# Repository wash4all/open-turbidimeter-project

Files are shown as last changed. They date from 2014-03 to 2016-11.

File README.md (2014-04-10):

# The Open Turbidimeter Project

## Contents
- [Background](#background)
- [What is "Turbidity"?](#what-is-turbidity)
- [Measuring Turbidity](#measuring-turbidity)
- [Goals for the Turbidimeter](#goals-for-the-turbidimeter)
- [Connectivity](#connectivity)
- [Development and Dependencies](#development-and-dependencies)
- [Licensing](#licensing)
- [Funding Sources](#funding-sources)
- [Contact](#contact)

## Background

The high cost of equipment to monitor water quality often puts valuable health tools out of reach for many communities in developing countries. Consequently, millions of people are exposed to health risks that could me mitigated if solutions were available at a price point they can afford. **The goal of our project is to create a low-cost device to measure the turbidity of a water supply.**

## What Is "Turbidity"?

Turbidity refers to the dirtiness or cloudiness of a water sample, and an internationally recognized criterion for assessing drinking water quality because the colloidal particles in turbid water may harbor pathogens, chemically reduce oxidizing disinfectants, and hinder attempts to disinfect water with ultraviolet radiation. Technicians at water treatment plants regularly measure water turbidity before and after treatment. It’s a legal requirement in many countries, and one indicator of whether treated water is safe for human consumption. The unaided eye can distinguish cloudy water from clear water, but even visibly clear samples of water can be dangerous.

## Measuring Turbidity

The quantification of turbidity is complicated by the fact that the goal is to obtain an aggregate quasi-concentration of *all* the different types of particles present in the water. This is different than, say measuring the concentration of a *specific* chemical by adding known quantities of reagents and measuring the mass of the resulting precipitate.

A turbidimeter is an optical instrument that assesses turbidity by measuring the scattering of light passing through a water sample. The general principle is that the more particles are floating around in the water, the more light will be scattered as it passes from on one side of a sample to the other. In its simplest form, a turbidimeter is just a light source and a photosensor arranged perpendicular to each other around a water sample. More complicated setups using multiple sensors and/or light sources extend the detection limit and accuracy of the device. Some possible layouts are shown below.

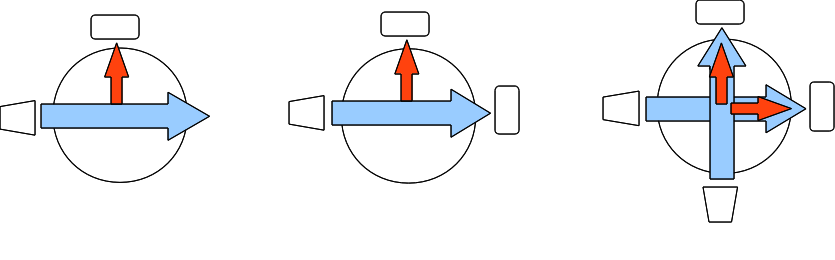
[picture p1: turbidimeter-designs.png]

*Source:* [turbidimeter-designs.png](turbidimeter-designs.png)

Turbidity is most commonly quantified by the Nephelometric Turbidity Unit (NTU)**\***. The NTU scale is defined by reference standards which are created by diluting approved compounds to concentrations designated by the [EPA][EPA Method 180.1] and [ISO][ISO 7027]. The primary standard for this scale is formazin, although other (safer) secondary standards have been approved. Note that these regulations have additional stipulations such as the measurement angle and wavelength of the light source. Looking over the standards themselves is *highly recommended.*

The human eye can detect turbidity levels down to roughly 5 or 10 NTU. Samples of water with turbidity lower than this will appear clear, but may still contain a concentration of colloidal particles sufficient to impair disinfection efforts and may carry a load of contaminants or pathogens sufficient to cause serious human illness. Current EPA regulations stipulate that conventionally treated surface water in the USA must be regularly sampled, that only 5% of samples in a given month may show turbidity greater than 0.3 NTU, and that no sample may show turbidity in excess of 1.0 NTU. Other countries employ different standards, and the World Health Organization (WHO) recommends that turbidity levels be less than 0.1 NTU prior to disinfection.

Handheld units capable of analyzing a single sample vial cost several hundred dollars; automated units capable of intermittently analyzing samples from flowing water can cost several thousand. Partly completed open-source turbidimeter projects can be found online, apparently abandoned.

**\*** Nephelometry is the term given to the side-scatter method of measuring turbidity described above

[EPA Method 180.1]: (http://water.epa.gov/scitech/methods/cwa/bioindicators/upload/2007_07_10_methods_method_180_1.pdf)
[ISO 7027]: http://www.iso.org/iso/catalogue_detail.htm?csnumber=30123

## Goals for the Turbidimeter

1.  Costs less than $100 when economies of scale are applied to production
2.  Reads samples with an accuracy of:
    1.  0.05 NTU from 0-5 NTU
    2.  0.2 NTU from 5-20 NTU
    3.  5% from 20-1000 NTU
3.  Can be operated manually or in automated sampling mode
4.  Has wireless data transmission capability
5.  Uses a replaceable battery pack

An open-source turbidimeter fulfilling the design goals listed above will not quite meet the strict technical requirements of the EPA, but will nonetheless provide a huge improvement over the status-quo of rural and small-scale water treatment monitoring, at a realistic cost.

## Connectivity

The intent is for these devices to be deployed at rivers, wells, and treatment plants in possibly very remote areas that are visited infrequently by engineers and regulators from more urban areas. For this reason, the device will be integrated with a remote data-acquisition system to enable record keeping, troubleshooting, and real-time observation of water quality. We are exploring a few different ways of getting data off the device wirelessly.

**Bluetooth** ```tested``` ```firmware support```
Include a low-power Bluetooth module that sends data to a linked Android cellphone, which uses its data plan and SMS to sync to a remote server. The problem with this is that the cost of a smartphone doubles or triples the cost of the device. The phone itself is also subject to damage or theft, which cripples the data connection. The additional processing power and memory afforded by a smartphone, on the other hand, are attractive features.

**GSM Modem** ```tested``` ```firmware support```
Integrate a GSM modem (the core piece of technology used by mobile phones) into the turbidimeter itself to provide wireless connectivity. This is a less expensive approach, but has issues with reliability and increases power consumption *quite a bit*. We also want to encourage DIYers to build their own units, and prototyping GSM modules like the one sold by Arduino are still not cheap. Therefore we want to make sure that the turbidimeter can still be used without wireless capability if we go with this approach.

**Direct Connection to Mobile Phone** ```not tested``` ```no firmware support```
Connect the turbidimeter to an arbitrary mobile phone using a wired connection. This requires the hardware to support the connection (most likely a USB host adapter), but in theory any GSM-compliant phone would be controllable using it. Here's an example of an [Arduino-controlled Motorola Razr](https://www.circuitsathome.com/mcu/programming/interfacing-arduino-to-a-cellular-phone).

## Development and Dependencies

In the prototyping stage, most of the development is done using rapid prototyping tools like Arduino and 3D printed parts. We expect to transition off these tools soon as we finish designing custom components, although it will always be possible to build your own turbimeter by printing the parts and assembling the necessary circuitry.

A list of software and hardware dependencies is maintained in the file [Dependencies.md](Dependencies.md). We try to use all open-source design tools, although we are stuck with a few non-free packages at the moment. For these cases, we export to open formats (such as STL, STEP, and BRD).

Issue tracking, package releases, and the like are managed through GitHub, which is most likely where you are reading this anyways. To download the revision-controlled repository with all the latest code, use ```git clone https://github.com/wash4all/open-turbidimeter-project.git```. Alternately you can browse the [releases][] for a stable set of files that are known to work.

[releases]: https://github.com/wash4all/open-turbidimeter-project/releases

## Licensing

The software and documentation for the project are covered by the [GNU General Public License][gpl] and [Creative Commons ShareAlike-Attribution][cc] licenses, respectively.

[gpl]: https://www.gnu.org/copyleft/gpl.html
[cc]: https://creativecommons.org/licenses/by-sa/4.0/

## Funding Sources

The Open Turbidimeter Project has been funded in part by EPA Grant Number [SU835517][grant]: "Smart" Turbidimeters for Remote Monitoring of Water Quality.

[grant]: http://cfpub.epa.gov/ncer_abstracts/index.cfm/fuseaction/display.abstractDetail/abstract/10094/report/0

## Contact

Development of the Open Turbidimeter Project is facilitated by [WASH for All][], an organization working for universal access to clean drinking water and sanitation by developing innovative and cost-effective tools.

Contact [Chris][] or [Alex][] if you'd like to get involved with WASH for All or if you have questions about the project or the organization.

[WASH for All]: http://wash4all.org
[Chris]: mailto:iamchriskelley@gmail.com
[Alex]: mailto:amk283@cornell.edu

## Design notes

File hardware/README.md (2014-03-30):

# Construction and Usage of the Turbidimeter

## Introduction

The sections below detail the necessary parts and tools, wiring, assembly, and microcontroller programming to get up and running with the Open Turbidimeter Project. You are encouraged to contact the team members with any questions about the construction, operation, or expansion of this device.

## Components List

All components of the open-source turbidimeter are indicated in the [Parts List](Parts List.tsv), along with potential
distributors. Indicated costs are for individual pieces and do not include shipping and handling or taxes.

## Structural Components

The open-source turbidimeter case consists of four different parts: (1) bottom, which includes ports for button and on/off switch; (2) cuvette holder, which houses the sensor and light source and holds the glass cuvette during device operation; (3) top, which has openings for the seven-segment LED display and the top of the cuvette holder; and (4) battery lid, which slides out from the case assembled case top and bottom to expose the battery holder. Electronic files of these objects (in STL format) are available in the [3D Design Files](3D Design Files/) folder. Note that any container that provides good shielding from incidental light may suffice for the larger portion of the case (e.g. a nested pair of cardboard boxes).

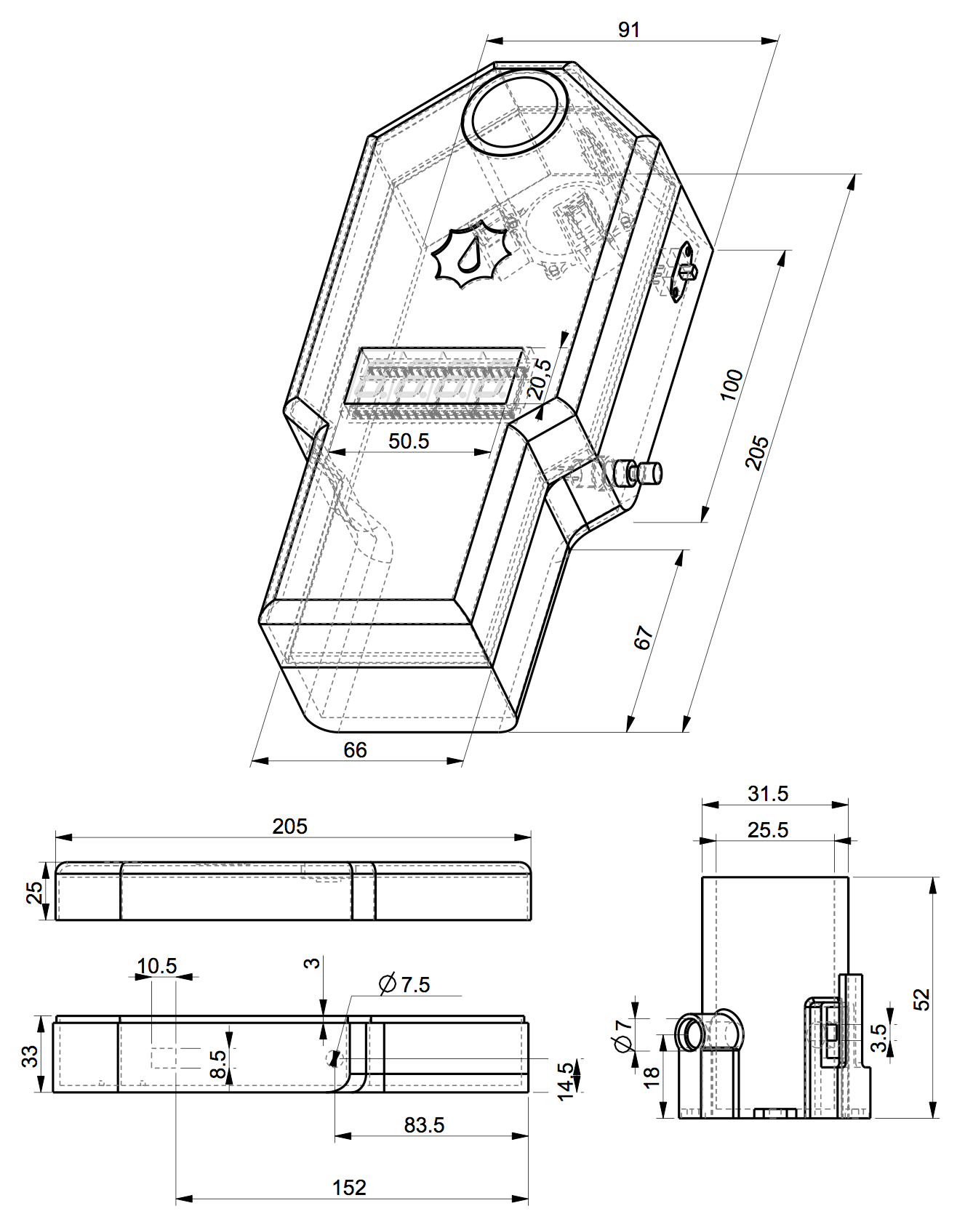
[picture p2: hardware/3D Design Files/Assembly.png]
Assembly

Link: [Assembly.png](3D Design Files/Assembly.png)

_**Fig 1** Image of the open-source turbidimeter with major dimensions given. The four smaller images (left to right) are the case lid (top left), the case base (bottom left), the battery lid (top right), and the cuvette holder (bottom right). All dimensions are in millimeters._

## Tools

A utility knife, soldering iron, and solder are required for assembly of the open-source turbidimeter, and safety goggles are recommended. To replicate the printed four-part case, one must have access to a 3D-printer with black ABS filament. The microprocessor can be programmed via a USB-to-Serial adapter (Mouser carries one [#A000059] for $14.95) or with an Arduino (as described in this [tutorial](http://arduino.cc/en/Tutorial/ArduinoToBreadboard). Electrical tape is very helpful (for grouping wires
together), as are a pair of wire strippers.

## Turbidimeter Breadboard and Schematic

The microprocessor and connected components of the open-source turbidimeter are depicted below in Fritzing (Figure S2) and EAGLE formats (Figure S3). Figure S2 depicts what the device looks like internally, while Figure S3 is a more formal schematic.

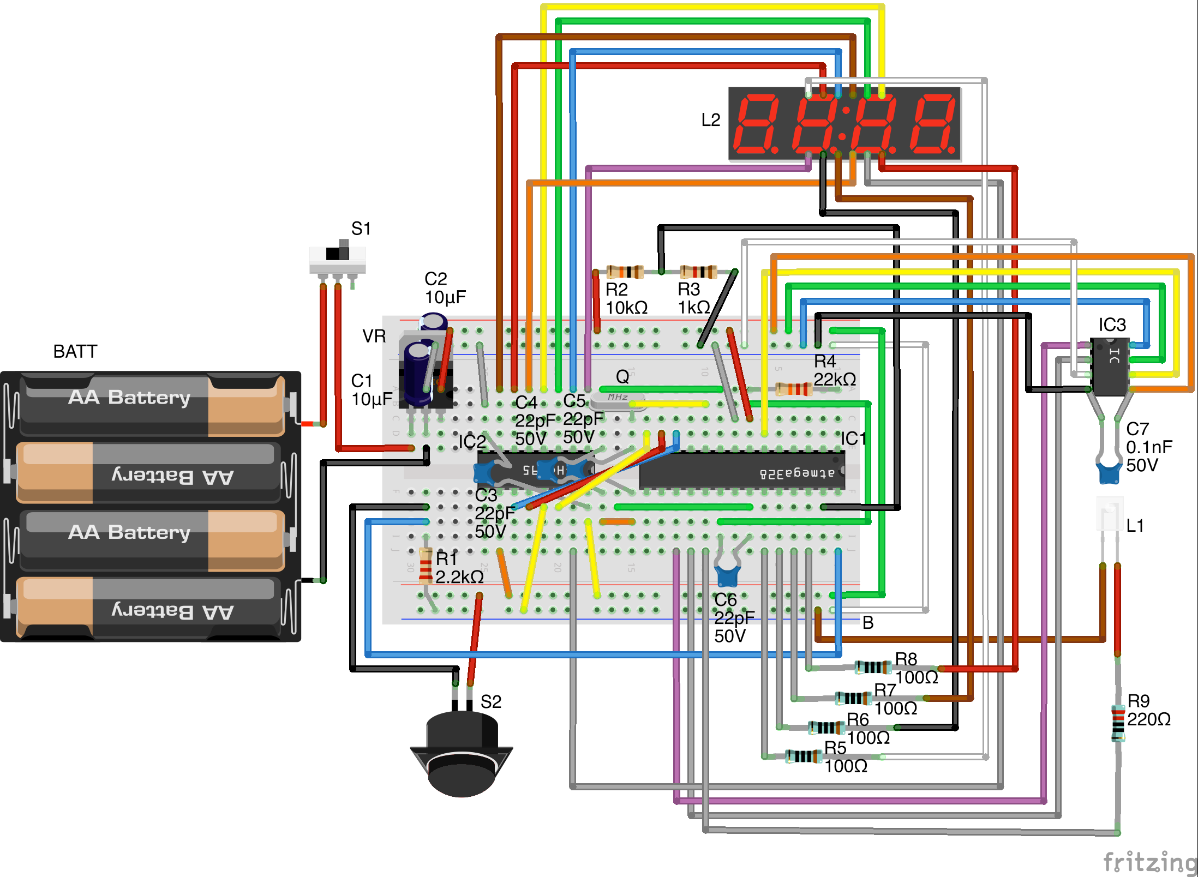
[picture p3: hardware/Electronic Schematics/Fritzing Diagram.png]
Fritzing Diagram

Link: [Fritzing Diagram](Electronic Schematics/Fritzing Diagram.png)
	
_**Fig 2** Depiction of the internal components of the open-source turbidimeter (components labels cross-referenced in the parts list and Figure S3)_

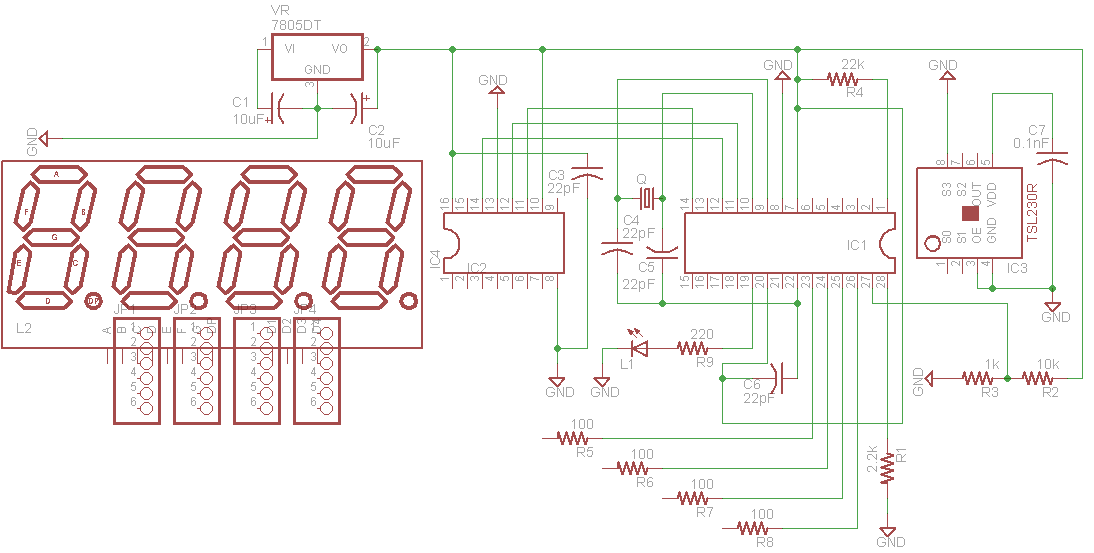
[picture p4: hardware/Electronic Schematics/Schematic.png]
Circuit Schematic

Link: [Circuit Schematic](Electronic Schematics/Schematic.png)

_**Fig 3** Schematic of the circuit board for the open-source turbidimeter (components labels cross-referenced in Table S1 and Figure S2)._

## Basic Assembly Instructions

1.  Gather the components listed in Section 1, and the tools listed in Section 3.
2.  Print the parts described in Section 2 (or devise your own light-shielding case).
3.  Wire together the internal components of the open-source turbidimeter according to Figures 2 and 3. Here are some key points:
    1.  It's hard to see some connections of the circuit, such as the wiring of the voltage regulator (VR1), on Figure 2. The Arduino website has a well-illustrated tutorial on wiring the ATMega328P microprocessor (http://arduino.cc/en/Main/Standalone) that the reader may find useful.
    2.  The semi-circles on the microprocessor (IC1) and shift register (IC2) indicate orientation of these components. It is vital that chips are aligned properly using these guides. Wiring them in the opposite orientation will destroy the chips once voltage is applied! Please note that the semi-circle on the TSL230R sensor in Figure 2 is merely a visual aid, and is not present on the actual chip.
    3.  The pins of the seven-segment display are diagrammed by the distributor Electrodragon (http://www.electrodragon.com/w/index.php?title=7-Segment_Display). The linked document maps pin placement to function and representation in Figure 3 (e.g., the bottom left pin on the seven-segment display is pin 12, which maps to segment E of the display, which connects to port QE on the shift register).
    4.  Resistors R2 and R3 combine to form a voltage divider, which is used to measure the voltage provided by the batteries. To achieve useful results, use resistors with tolerance of 1% or less. Tolerance levels of 5% are suitable for the other resistors in the device.
    5.  The internal components list generally should be followed closely, however the power switch (S1) and button (S2) can easily be changed to suit the builder's aesthetic.
    6.  As always, exercise caution. Do not attempt construction of any electrical device without knowledge of proper technique and safety.

## Programming

The files included in the ```software``` folder of the project need to be compiled and uploaded to the microcontroller to get the device working. Connect the device to a computer using a properly wired [USB-to-Serial adapter](http://arduino.cc/en/Main/USBSerial) (this requires the use of an additional 100nf capacitor) or an [Arduino board](http://arduino.cc/en/Tutorial/ArduinoToBreadboard). Then install the [Arduino programming environment](http://arduino.cc/en/main/software). After followng the instructions in the sofware readme to install the necessary libraries, open the ```turbidimeter.ino``` program in the Arduino software and upload it to the microcontroller.

You're ready to go!

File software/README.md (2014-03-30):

# Software

This directory contains the _firmware_ for the turbidimeter. These are the files that are compiled and uploaded to the microcontroller and provide the user interface, measurement, and calibration functions.

Contents:

The folder called ```turbidimeter``` is the [Arduino](http://arduino.cc/en/main/software) project folder for the turbidimeter firmware. This can go anywhere and you can rename it, but the ```.ino``` file must have the save name as the parent folder when working in the Arduino IDE. This is the file that you most likely be working with if you want to change how the turbidimeter operates.

The ```libraries``` folder contains the extra libraries needed to compile the Arduino sketches, providing the ability to send/receive text messages, store calibration data, etc. These need to be made available to the Arduino compiler by putting them in a place it knows about. One sure way to do this is to import them using the "Sketch>Import Library" utility in the Arduino IDE. Depending on how you have installed Arduino, this should have the effect of copying the files into the ```C:/Users/You/Documents/Arduino/libraries``` folder (Windows) or ```~/sketchbook/libraries``` folder (Mac/Linux). Note that some of the libraries have the same name as those prepackaged with the Arduino software. They are different (usually slightly modified for interoperability reasons); if you run into errors, make sure you are using the right ones.

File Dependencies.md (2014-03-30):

# Guide to File Extensions

A list of the file types you may encounter in this project. We have attempted to restrict the software dependencies to free programs as much as possible, with a few exceptions (and we are working on those).

-  ```.sch``` [Eagle](http://www.cadsoftusa.com/eagle-pcb-design-software/?language=en) circuit schematic
-  ```.brd``` [Eagle](http://www.cadsoftusa.com/eagle-pcb-design-software/?language=en) printed circuit board file
-  ```.ods``` Open Document Spreadsheet file (supported by Excel, LibreOffice, etc.)
-  ```.stl``` 3D part file that can be used to send parts to a 3D printer or production service
-  ```.scad/escad``` [OpenSCAD](http://www.openscad.org)/[extended OpenSCAD](http://www.implicitcad.org) code used to generate 3D part files
-  ```.part``` Proprietary [PTC Creo](http://www.ptc.com/product/creo/) CAD file. We try to provide open source equivalents to these files as much as possible, because CAD software can be very expensive.
-  ```.md ``` [Markdown](https://help.github.com/articles/markdown-basics) file. Just a text file with standardized syntax for headings and things. 
-  ```.ino``` [Arduino](http://www.arduino.cc) program
-  ```.c/.h/.pde``` C source files for Arduino libraries

**See also:** [Parts List](hardware/Parts List.tsv)

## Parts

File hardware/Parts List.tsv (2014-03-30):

Qty | Name | Description | Vendor | Part # | Unit Price | Price
1 | IC1 | 8-bit Microcontroller | Mouser Electronics | ATMEGA328P-PU | 2.24 | 2.24
1 | Q1 | 16MHz 18pF HC49S Crystals | Mouser Electronics | HC49US-16.000MABJ-UB | 0.58 | 0.58
1 | VR1 | 5V Voltage Regulator | Mouser Electronics | LM7805CT | 0.69 | 0.69
1 | IC2 | 595 Shift Register | Mouser Electronics | SN74HC595N | 0.63 | 0.63
2 | C1,2 | 10uF Capacitor | Mouser Electronics | UKL1C100MDD1TA | 0.15 | 0.3
4 | C3-6 | 22pF Capacitor | Mouser Electronics | 1C10C0G220J050B | 0.015 | 0.06
1 | C7 | 0.1nF Capacitor | Mouser Electronics | 140-50S5-101J-RC | 0.06 | 0.06
1 | R1 | 1/4 Watt 2.2 kOhm Resistor | Mouser Electronics | MF1/4DCT52R2201F | 0.06 | 0.06
1 | R2 | 1/4 Watt 10 kOhm Resistor | Mouser Electronics | MF1/4DCT52A1002F | 0.06 | 0.06
1 | R3 | 1/4 Watt 1 kOhm Resistor | Mouser Electronics | MFS1/4DCT52R1001F | 0.13 | 0.13
1 | R4 | 1/4 Watt 22K Ohm Resistor | Mouser Electronics | MF1/4LCT52R223J | 0.07 | 0.07
4 | R5-8 | 1/4 Watt 100 Ohm Resistor | Mouser Electronics | MF1/4DC1000F | 0.06 | 0.24
1 | R9 | 1/4 Watt 220 Ohm Resistor | Mouser Electronics | MF1/4CCT52R2000F | 0.14 | 0.14
1 | B1 | Breadboard* | Electrodragon | 5205940 | 0.23 | 0.23
1 | - | M/F Jumper Wires (22 count) | Electrodragon | 5101606 | 1.2 | 1.2
1 | S2 | Black Button | Mouser Electronics | 104-0013-EVX | 0.91 | 0.91
1 | L1 | 860nm Infrared LED | Mouser Electronics | W53SF6C | 1.12 | 1.12
1 | L2 | 7-Segment Display | Electrodragon | 4103417 | 0.35 | 0.35
1 | IC3 | TSL230R Sensor | A-Wit | CS454000 | 5.94 | 5.94
1 | BATT | 4xAA Battery Holder | Mouser Electronics | 12BH348-GR | 1.15 | 1.15
1 | - | Printed Cuvette Holder** | -- | -- | 1.42 | 1.42
1 | - | Printed Turbidimeter Encasing** | -- | -- | 7.55 | 7.55
2 |  | Glass Cuvette – 27mm diameter | (Various) | -- | 0.5
1 |  | GSM Modem | Mouser Electronics | A000043 | 88.95

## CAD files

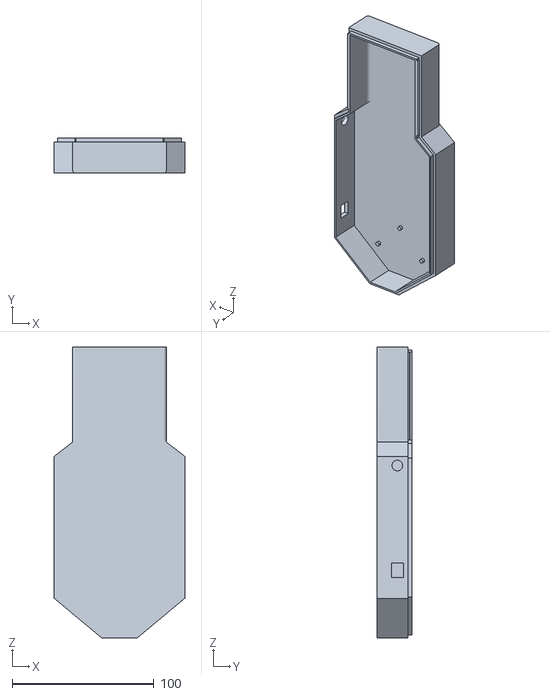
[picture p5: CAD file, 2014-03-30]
hardware/3D Design Files/case_bottom.stl
92.0 x 25.0 x 205.0

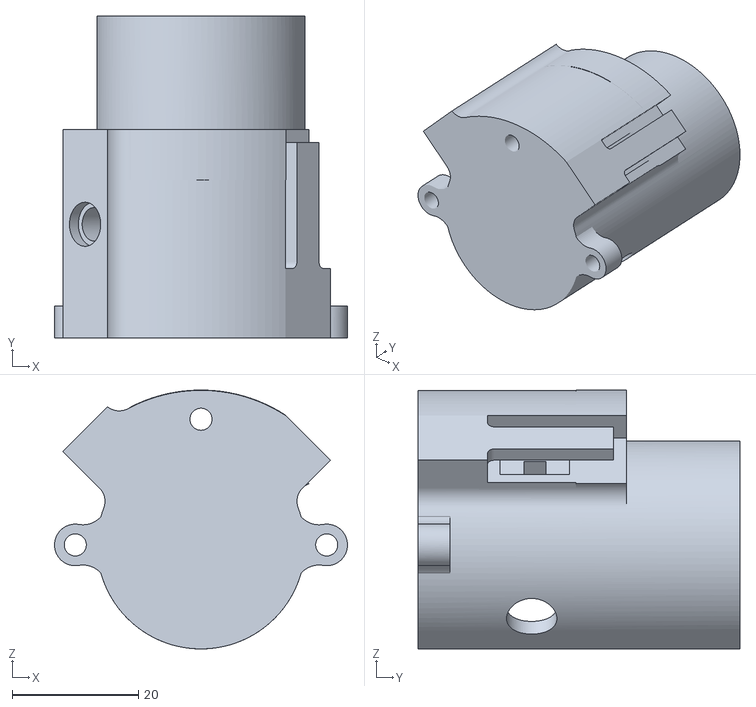
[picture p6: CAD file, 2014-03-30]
hardware/3D Design Files/sample_chamber.stl
46.5 x 51.0 x 41.1

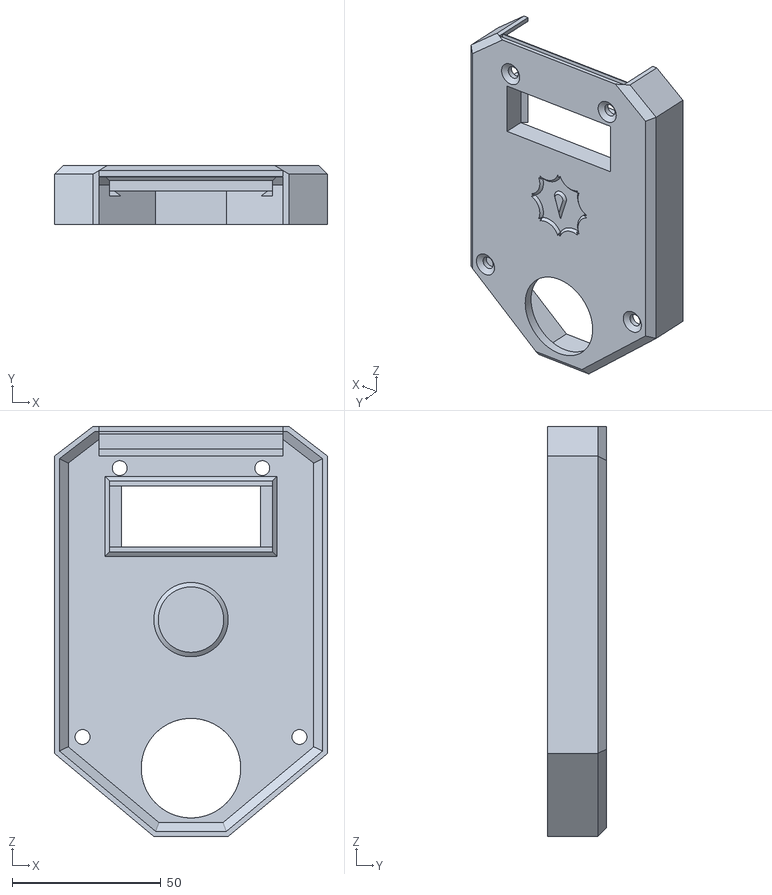
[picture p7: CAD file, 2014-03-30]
hardware/3D Design Files/case_top.stl
92.0 x 20.0 x 138.0

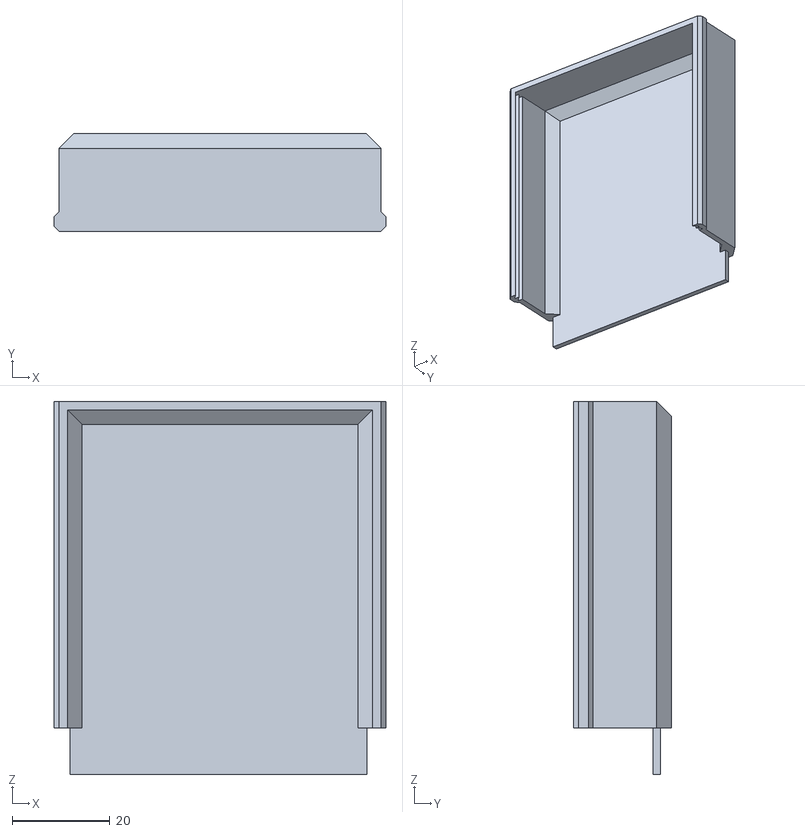
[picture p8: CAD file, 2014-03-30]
hardware/3D Design Files/battery_cover.stl
68.0 x 20.0 x 76.5

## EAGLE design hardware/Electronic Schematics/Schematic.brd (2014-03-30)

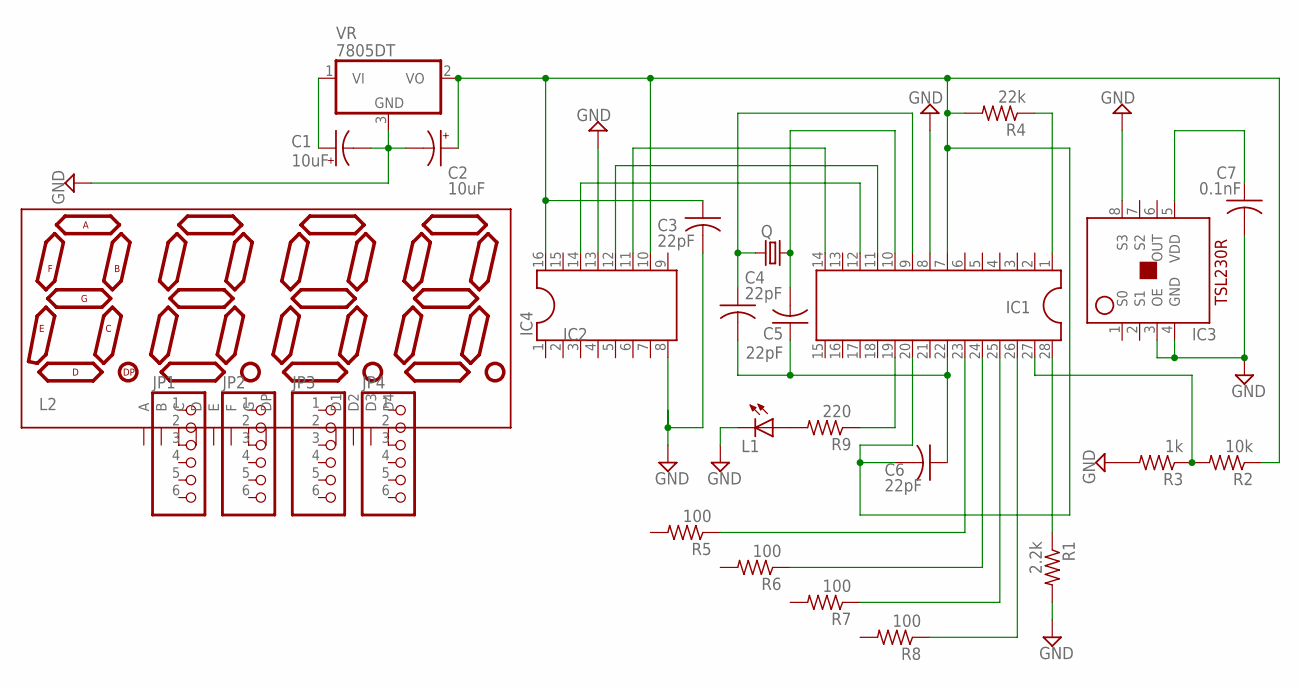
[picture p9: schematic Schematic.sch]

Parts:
C1, C2: 10uF; 140CLH-1010
C3, C4, C5, C6: 22pF; C025-024X044
C7: 0.1nF; C025-024X044
IC1: DIL28; DIL28-6
IC3: LIGHT_TO_FREQ_CONVERTER
IC4: DIL16
JP1, JP2, JP3, JP4: PINHD-1X6CLEAN; 1X06-CLEAN
L1: LEDIRL80A; IRL80A
Q: CRYSTALHC49S; HC49/S
R1: 2.2k; 0207/12
R2: 10k; 0207/12
R3: 1k; 0207/12
R4: 22k; 0207/12
R5, R6, R7, R8: 100; 0207/12
R9: 220; 0207/12
U$1: 7-SEGMENT-4DIGIT-COUNTERPTH; 7-SEGMENT-4DIGIT-COUNTER
VR: 7805DT; TO252

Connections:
GND: C1.-, C2.-, C3.2, C7.2, IC1.8, IC3.3 (OE), IC3.4 (GND), IC3.8 (S3), IC4.8, IC4.13, L1.K (C), R1.2, R3.2, VR.3 (GND)
unnamed: IC1.24, R6.1
unnamed: IC1.23, R5.1
unnamed: IC1.25, R7.1
unnamed: IC1.26, R8.1
unnamed: IC1.28, R1.1
unnamed: IC1.19, R9.1
unnamed: L1.A, R9.2
unnamed: IC1.11, IC4.12
unnamed: C4.2, C5.1, C6.1, IC1.22
unnamed: C1.+, VR.1 (VI)
unnamed: JP1.3, U$1.4 (C)
unnamed: IC1.12, IC4.14
unnamed: C4.1, IC1.9, Q.2
unnamed: C2.+, C3.1, C6.2, IC1.7, IC1.20, IC4.10, IC4.16, R2.1, R4.2, VR.2 (VO)
unnamed: IC1.1, R4.1
unnamed: IC1.14, IC4.11
unnamed: C7.1, IC3.5 (VDD)
unnamed: JP2.3, U$1.5 (G)
unnamed: JP4.3, U$1.6 (D4)
unnamed: IC1.27, R2.2, R3.1
unnamed: C5.2, IC1.10, Q.1

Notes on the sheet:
IC2
IC3

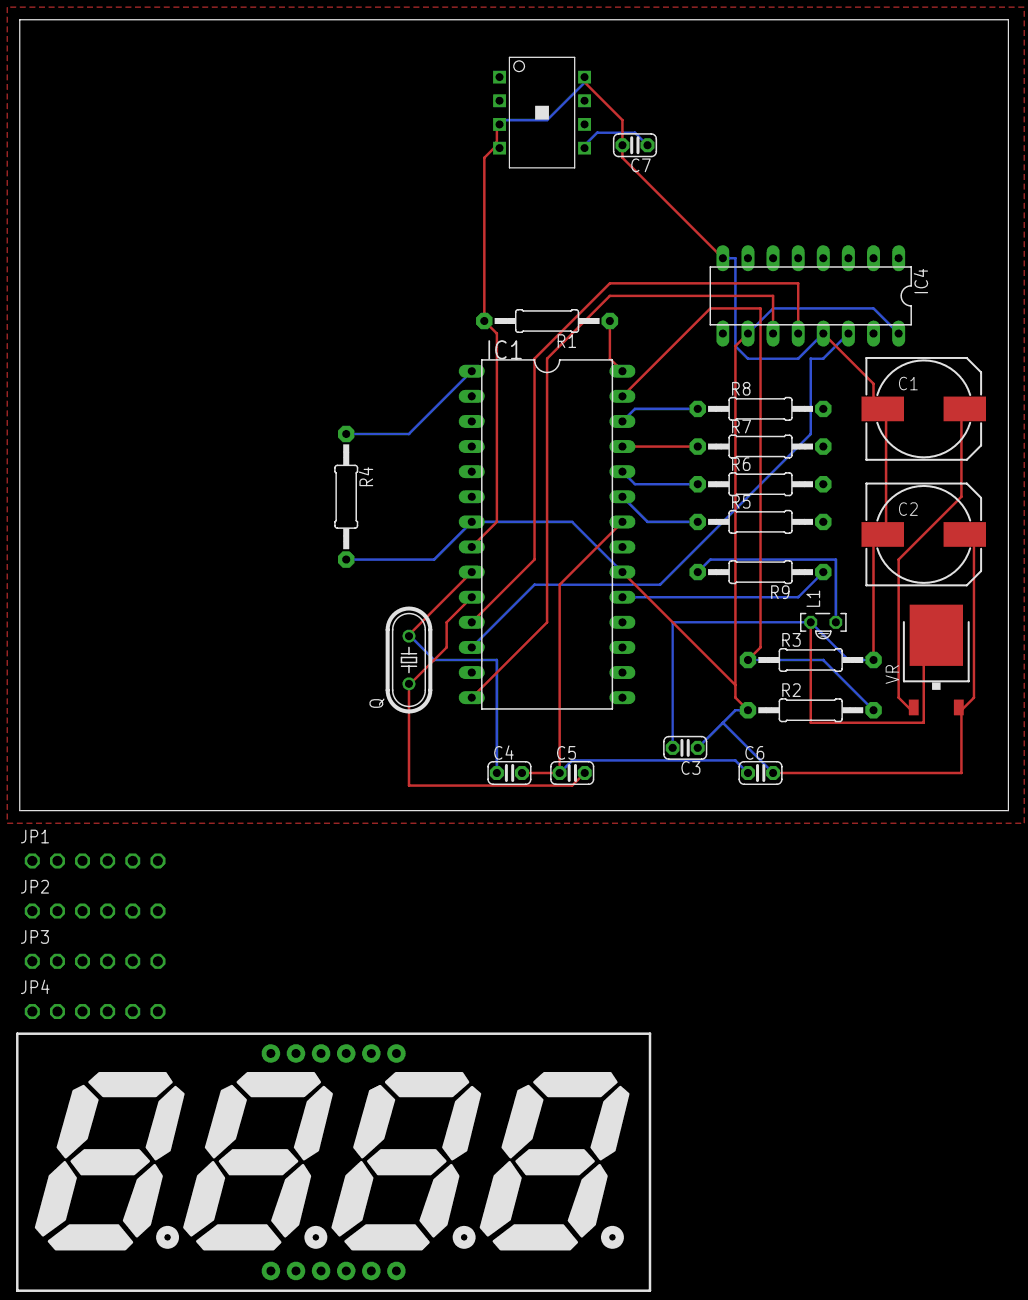
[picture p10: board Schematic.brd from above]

Board: 2 copper layers, 100.0 x 80.0 mm, 27 parts (0 on the bottom side), 22 nets.

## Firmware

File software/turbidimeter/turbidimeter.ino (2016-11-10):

/*--------------------------OPEN TURBIDIMETER PROJECT------------------------*/
/*------------------------------- ARDUINO CODE ------------------------------*/
/*---Developed by WASH4All, 2014. See wash4all.org for further information.--*/

// Flags
const boolean debug=false;  // to reset memory to default config -> true
const boolean using_modem=false; // if not using a GSM modem, change to false
  
// Libraries
// NOTE: Be sure to use the libraries included with this sketch
// (by placing them in your Arduino or Sketchbook folder)
#define NO_PORTD_PINCHANGES
#define NO_PORTC_PINCHANGES
#include <GSM.h>
#include <PinChangeInt.h>
#include <EEPROM.h>
#include <EEPROMAnything.h>
#include <avr/interrupt.h>
#include <avr/power.h>
#include <avr/sleep.h>
#include <avr/io.h>

// Definitions
#define PINNUMBER "1111" // PIN Number for SIM card
#define VERSION_BYLINE "Open Turb Prj\nBIOS v1.11\n2014-04-08\n"
#define IR_LED    4    // light source
#define TSL_S1   12    // S1 and S0 are pins on the TSL230R chip
#define TSL_S0   11
#define TSL_FREQ 13    // frequency signal from the sensor
#define BPIN     A5    // external button
#define BUTTON_EVENT_VALUE 1000

/* 
   Change boolean value, and switch out commented and uncommented the following two 
   pairs of lines below to switch from common cathode to common anode seven-segment display
   NB: For the seven-segment display listed in the Supplementary Materials document, to distinguish
   common cathode and common anode models, look on the side of the display for the numbers '0.56'. 
   If that number is followed by a plus () sign, the display is common cathode.
*/

#define common_cathode_display 1 //if using a common-anode seven segment display, change to false (0)
#if common_cathode_display
#define SEVEN_SEG_NUMBERS {B11000000,  B11111001,  B10100100,  B10110000, B10011001,  B10010010,  B10000010,  B11111000, B10000000,  B10010000,  B01111111,  B10111111, B11111111}
#define SEVEN_SEG_LETTERS {B10101111,  B10000110,  B10100001,  B10010001, B11000111,  B10010010,  B10000111,  B11000000}
#else
#define SEVEN_SEG_NUMBERS {B00111111,  B00000110,  B01011011,  B01001111, B01100110,  B01101101,  B01111101,  B00000111, B01111111,  B01101111,  B10000000,  B01000000, B00000000}
#define SEVEN_SEG_LETTERS {B01010000,  B01111001,  B01011110,  B01101110, B00111000,  B01101101,  B01111000,  B00111111}
#endif

// Gauge voltage by comparison to ATMega328P's internal 1.1v
// R1 and R2 form a voltage divider, with V_out = V_in * R2 / (R1  R2)
#define VPIN     A4    // read voltage from this pin
#define DIV_R1 10000   // resistance for R1
#define DIV_R2  1000   // resistance for R2
#define SAMPLING_WINDOW 1000    // milleseconds between frequency calculations
#define HIGH_SENSITIVITY  100   // sensitivity settings, set via S0 and S1 pins
#define MED_SENSITIVITY   10    // ...
#define LOW_SENSITIVITY   1     // ...
#define READ_REPS 6    // number of readings the turbidimeter will take per 
// button press (average is used for reporting)

// Set up GSM library
GSM gsmAccess;  //US band:"GSM850_EGSM_DCS_PCS_MODE"
GSM_SMS sms;
boolean notConnected = true;

// Global Vars
int  scale_divider = 2, sensitivity = HIGH_SENSITIVITY;     
// scale_divider must match hardwired TSL_S2 and TSL_S3 settings, 
// sensitivity sets TSL_S0 and TSL_S1 settings
// see TSL230R user's guide for more information
int bpress = 1023;   
//variable for digital mapping of analog button press event
float div_fact = 1;  
//division factor, to normalize sensor output by voltage level
long freq_jump_hi = 50000, freq_jump_lo = 4000;            
// (These settings could be used to dynamically set sensor sensitivity,
// e.g. for detecting very bright light levels)
unsigned long timer, frequency;                              
volatile unsigned long pulse_count = 0;  
//interrupt variable; stores count data coming from sensor
boolean bpressed = false, sufficient_battery = true;
const int num_displays = 4;                                  
const int shift_latch = 5;  // RCLK                           
const int shift_clock = 8;  // SRCLCK
const int shift_data = 6;   // SER
// The above three pins connect the 74HC595 shift register
const int dispPorts[num_displays] = {A3,A2,A1,A0};
String language = "espanol"; //"english";
char serialInput;

// Characters: 0-9, '.', '-', blank                   
const byte SevenSegNumbers[13] = SEVEN_SEG_NUMBERS;
  
// Characters: rEdYLStO
const byte SevenSegLetters[8] =  SEVEN_SEG_LETTERS;

// Use this structure for storing data & retrieving data persistently in EEPROM
struct config_t{
  int foo;           //example
  long machine_id;   //example
  unsigned long last_calibration_timestamp; // in seconds since 1/1/1970 12:00a
  // define calibration constants for 5 calibration curves
  // y is the lower bound, m is the slope, b is the the y-intercept (y=mxb)
  float y0, y1, y2, y3, y4,
  m0, m1, m2, m3, m4,
  b0, b1, b2, b3, b4;
  char* remoteNum;
  char* selfNum;
  String userfn; // First name of the person using the device
  String useremail; // Email address of the person using the device
  char* userpn; // Phone number of the person using the device
  String username; // Username for Open Source Water server
  String password; // Password for Open Source Water server
} config;

/*---------------------------------------------------------------------------*/
/*--------------------------------FUNCTIONS----------------------------------*/
/*---------------------------------------------------------------------------*/

void setup() {
  // Set up serial commication
  Serial.begin(9600);
  Serial.println(VERSION_BYLINE);
  Serial.println("Press r to read, c to calibrate.");
  // Pin I/O settings
  pinMode(TSL_FREQ, INPUT); // light sensor
  pinMode(TSL_S0, OUTPUT);  // light sensor
  pinMode(TSL_S1, OUTPUT);  // light sensor
  pinMode(IR_LED, OUTPUT);  // light source
  pinMode(BPIN, INPUT); // button
  pinMode(VPIN, INPUT); // voltage
  pinMode(shift_latch, OUTPUT); // shift register
  pinMode(shift_clock, OUTPUT); // shift register
  pinMode(shift_data,  OUTPUT); // shift register
  for(int i = 0; i < num_displays; i){
    pinMode(dispPorts[i], OUTPUT);
    // set display pins to output
  }

  // Startup procedure
  digitalWrite(IR_LED, LOW);  // light source off
  delay(200);
  turnOffDisplay();
  setSensitivity(sensitivity); // set sensor sensitivity
  timer = millis();
  displayForInterval(-1, "dashes", 1000);

  // Prepare sensors  
  if(divisionFactor_TSL230R() < 0){
    sufficient_battery = false;
    displayForInterval(-1, "error", 2000);
  }
  else{
    displayForInterval(-1, "ready", 2000);
    turnOffDisplay();
  }

  if(debug){
    config.foo = 255;                               
    config.machine_id = 11111111;
    config.last_calibration_timestamp = 1390936721;
    config.y0 = 0;                                  
    config.m0 = 0.02876;                              
    config.b0 = -2.224;                              
    config.y1 = 87.63;
    config.m1 = 0.039;
    config.b1 = -3.124;
    config.y2 = 276.94;
    config.m2 = 0.04688;
    config.b2 = -5.298;
    config.y3 = 2472.3;
    config.m3 = 0.05223;
    config.b3 = -18.525;
    config.y4 = 6049;
    config.m4 = 0.0721;
    config.b4 = -138.9;
    config.remoteNum = "14109278905";
    config.selfNum = "1410*******";
    config.userfn = "****";
    config.useremail = "***@****.org";
    config.userpn = "1410*******";
    config.password = "******";
    config.username = "******";
    
    EEPROM_writeAnything(0, config);
    // Write example calibration settings to EEPROM memory
  }
  else{
    EEPROM_readAnything(0, config);
    // Read calibration data from EEPROM memory
  }
}

void loop() {
  // Given there is enough battery power for the  sensor,
  // - read sensor value for given number of times,
  // - display the resulting value for 4000 milliseconds,
  // - clear out register pins, for a clean display next 
  //   time device is powered off/on.
  // - build a text message and transmit,
  // - check for and parse incoming messages,
  //   if using_modem flag is set to true.  
  // - check for incoming serial commands and process them.
  boolean sufficient_battery = true;
  float reading;
  if(sufficient_battery){
    // SERIAL CONTROL OPTIONS
    serialInput = 'x';
    if (Serial.available() > 0) {
      serialInput = Serial.read(); // get one-byte command option
      Serial.println((char)serialInput); // tell the user what they pressed
    }    
    // check for button press event (0 = pressed)
    bpress = analogRead(BPIN); 
    if (bpress >= BUTTON_EVENT_VALUE || serialInput == 'r'){
      bpressed = true;
      divisionFactor_TSL230R();                
      // read, but discard first reading
      div_fact = divisionFactor_TSL230R();     
      // take another reading of voltage divider
      if(div_fact < 0){
        Serial.println("Battery low...");
        sufficient_battery = false;
      }     
      else{ 
        Serial.println("Taking reading...");        
        reading = takeReadings(READ_REPS);
        Serial.print(reading); 
        Serial.print(" NTU\n");
        displayForInterval(reading, "data",4000);            
        displayForInterval(-1, "clear", 100);

        // GSM CONTROL OPTIONS
        if(using_modem){                                     
          int msg_len = 140;
          char txtMsg[msg_len];
          String bn, message_text;
          bn = baseNmap(reading);
          message_text = "#un " + (String)config.username +
                        " #pw " + (String)config.password +
                        " #reading " + bn;
          // This command as currently coded will send 
          // a coded text message of every reading!!
          openConnection();
          delay(10000);
          sendMessage(config.remoteNum, message_text);
          String incoming = getMessageText();
          parseMessage(incoming);
          closeConnection();
        } 
      }
    }
    else if(serialInput == 'c'){
      calibrate();
    }
    else if(serialInput != 'x'){
      Serial.println("Invalid input. Press r to read, c to calibrate.");
    }
    if(bpressed){
      bpressed = false; // reset
      turnOffDisplay();
    }
  }
  else{
    divisionFactor_TSL230R();
    displayForInterval(-1, "error", 500);
    turnOffDisplay();
    delay(500);
  }
}

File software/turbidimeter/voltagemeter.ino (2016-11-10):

/*--------------------------Voltage Meter Functions--------------------------*/
#define TEMP_PIN A4

float divisionFactor_TSL230R(){
  float m = .0052;   //slope of sensor's linear response curve
  float vmin = 3.0;  //min operating v of sensor
  float vmax = 5.5;  //max operating v of sensor
  float v100 = 4.9;  //voltage | normalized response of TSL230r = 1.0
  analogReference(INTERNAL); 
  delay(200); 
  float v = getVoltageLevel();
  analogReference(DEFAULT);
  delay(200); 
  if(v < vmin || v > vmax){
    return 1;
  }
  else{
    return 1 - (4.9 - v) * m;
  } 
}

float getVoltageLevel(){
  float sensorValue = analogRead(VPIN); //drop the first reading
  delay(100);
  sensorValue = float(analogRead(VPIN));
  float divider_value = float(DIV_R2) / float(DIV_R1+DIV_R2);
  float voltage = sensorValue/ 1023.0 * 1.1 / divider_value;  
  // normalize by max mapping value, internal reference voltage, 
  // and voltage divider, respectively.
  return voltage;
}

float getLightMultiplier(){
  //LED operating characteristics: temperature effect on light intensity (from user's manual)
  float led_voltage = 0.0, temp_base = 24, temp_slope = -.00473, temp_multiplier = 1.0;  
  //LED operating characteristics: voltage and current effect on light intensity (from user's manual)
  float led_vi = 1.4, li_base = 1.8125, li_slope = 17.9167, li_multiplier = 0.0;         
  //empirical curve of LED voltage and system voltage for open-source turbidimeter
  led_voltage = .0181 * getVoltageLevel() + 1.3376;                                         
  //calculate light intensity factor of LED due to voltage and current
  li_multiplier = ((led_voltage - led_vi) * li_slope + li_base) / li_base;               
  float temp = readLM35Temperature();
  //calculate light intensity factor of LED due to ambient temperature
  temp_multiplier = 1 + (temp - temp_base) * temp_slope;                    
  return li_multiplier * temp_multiplier;
} 

float readLM35Temperature(){
  analogReference(INTERNAL);
  delay(200);
  //with 10mV per degree C, and 1100mV for 1024 steps, scaling_factor = 10/(1100/1024) ~ 9.3
  float t =  analogRead(TEMP_PIN) / 9.3;             
  analogReference(DEFAULT);
  delay(200);
  return t;
}

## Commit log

2013-07-03 first GitHub commit
    [bottom_mold.SLDASM, case-bottom.fcstd, case-bottom.scad, case-bottom.stl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]
2014-02-11 Add parts list
    [Parts List.ods]
2014-02-11 Update turbidimeter.ino
    changed variable definitions for voltage divider, and add GSM-related comments in several places
2014-03-10 Create gsm_integration_code_update
    Not sure if I'm following protocol here properly, Alex. This is an updated version of the main INO file. Main changes are:
    -removed program control of the modem Rx pin (pin 3), which was hanging program flow
    -simplified the display functions, saving a lot of calculation (numbers are assigned to specific digits on the seven-segment only once, instead of each time they are flashed for POV)
    -correctly implemented the bit shift logic to allow easy swapout of common anode and cathode
    -put in a note on how to identify if a seven-segment display is common cathode or common anode
2014-03-27 add circuit schematic source files
    [turbidimeter_fritzing.brd, turbidimeter_fritzing.fzz]
2014-03-28 add assembly instructions and hardware files
    [Parts List.tsv, Schematic.brd, Schematic.sch, battery_cover.stl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]
2014-03-28 clear out old files
    [bottom_mold.SLDASM, case-bottom.fcstd, case-bottom.scad, case-bottom.stl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]
2014-03-28 fix documentation
    [Parts List.tsv]
2014-03-30 add calibration function
2014-03-31 remove extra lines from calibration code
2014-04-23 Update turbidimeter.ino
    correctly places Serial input in the program logic, and allows sample reading to be triggered either by Bluetooth or by button press.
2014-04-24 Update voltagemeter.ino
    adding temperature correction

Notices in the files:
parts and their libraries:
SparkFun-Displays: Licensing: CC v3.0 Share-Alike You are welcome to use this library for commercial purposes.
